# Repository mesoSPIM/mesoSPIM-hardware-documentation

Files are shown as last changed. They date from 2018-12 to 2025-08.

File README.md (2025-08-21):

## What is the mesoSPIM project?
The mesoSPIM (mesoscale selective plane illumination microscopy) project
aims at creating open-hardware microscopy platforms for imaging in cleared tissue. Core features of the mesoSPIM setups are:

* compatibilty with all tissue clearing techniques
* large field-of-views
* dual-sided excitation
* optimized for fast screening of whole mouse brain samples (10-14 GB/brain/color at low magnification, up to 100 GB/brain/color at high magnification)
* near-isotropic sampling (1.5-5 µm in X,Y and 3-6 µm in Z) due to an axially swept lightsheet which leads to uniform z-resolution across the field-of-view
* modular sample holders and quick sample exchange
* large travel range (50 x 50 x 100 mm) to allow imaging of very large samples

## Benchtop mesoSPIM
The [Benchtop mesoSPIM](https://github.com/mesoSPIM/benchtop-hardware) is the newest version and its repository is separate to organize documentation and wiki pages of the two very different systems.

## "Mainframe" mesoSPIM
The [mesoSPIM v.5 wiki](https://github.com/mesoSPIM/mesoSPIM-hardware-documentation/wiki) provides documentation, setup, and usage instructions of "mainframe" mesoSPIMs that require an optical table.

## mesoSPIM Version 6 "Revolver"
The detection arm of older versions (4 and 5) can be upgraded to a v.6 "Revolver" using the [following documentation](https://github.com/mesoSPIM/benchtop-hardware/tree/main/v4-5-upgrade-2023).

## mesoSPIM v.5
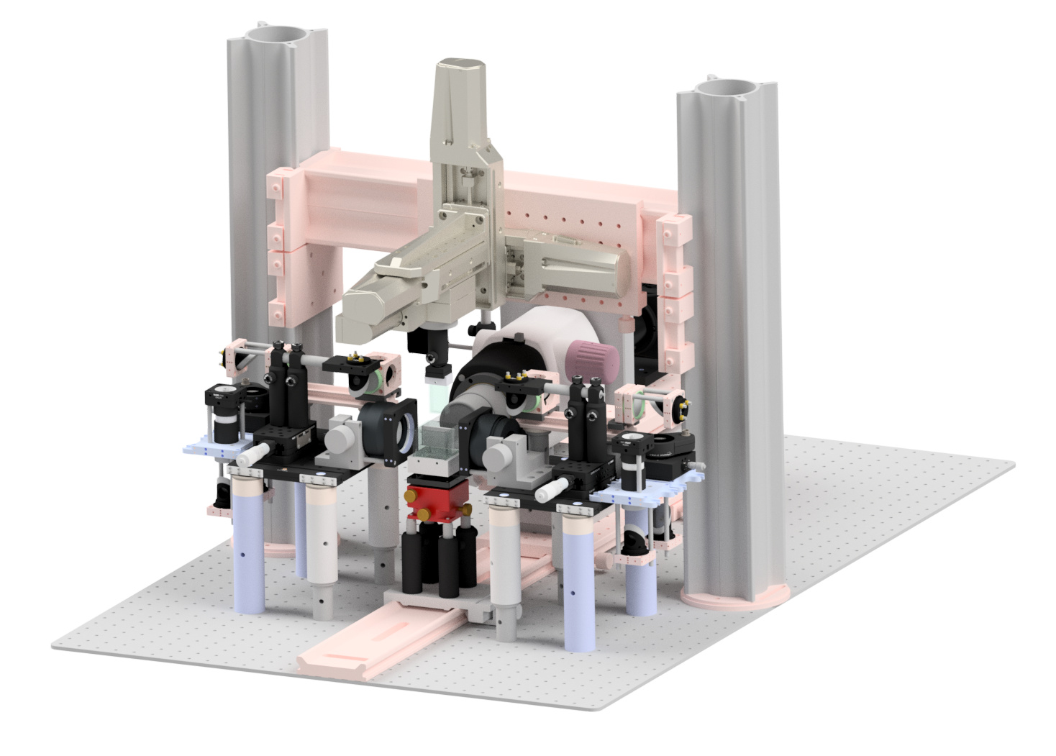
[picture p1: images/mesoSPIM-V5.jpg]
mesoSPIM V5


## Who is the mesoSPIM project for?
* You are looking for a versatile imaging platform for cleared tissue that can be tailored to your needs.
* Research groups and imaging facilities with experience in building and supporting custom microscopes.

## What are ideal imaging applications for a mesoSPIM?
* screening of large numbers of samples for clearing & labeling quality
* visualization of cell populations or other structures (blood vessels, plaques) in whole cleared organs

## What are the mesoSPIM instruments less well suited for?
* imaging live samples (this is the domain of classical light-sheet microscopes)
* high-resolution imaging (<1.5 µm optical resolution), e.g. subcellular structures.

## Not sure where to start?
You can start by comparing [Benchtop and V5](https://github.com/mesoSPIM/benchtop-hardware/tree/main) versions and deciding which one suites your needs better. When ready, review the respective Wiki pages and parts list. If still in doubt, contact us for help.

## About
See the project history and meet the developers on our [main website](https://mesospim.org/about/).

## Discussion
Since August 2025 we joined the vibrant [image.cs forum](https://forum.image.sc/tag/mesospim)



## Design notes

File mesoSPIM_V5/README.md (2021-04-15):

## Dimensional accuracy

Depending on manufacturing method, the dimensions of machined/3D printed part can deviate from the 
"perfect" fit to a glass cuvette or Thorlabs component.
Machined parts have dimensional accuracy typically 0.05 - 0.1 mm, 3D printed parts 0.1 - 0.2 mm 
and uneven surface finish.

Several iterations with dimension adjustment of model or part may be necessary to accomodate your 
particular manufacturing method.

For metal or plastic machining with [Protolabs](https://www.protolabs.com/), accuracy 0.1 mm should be expected.

For 3D printers (0.1-0.2 mm), see articles
* [3D Printer Dimensional Accuracy: 7 Tips & Tricks](https://all3dp.com/2/dimensional-accuracy-3d-printing-tips-tricks/).
* [Simplify3D: dimensional accuracy](https://www.simplify3d.com/support/print-quality-troubleshooting/dimensional-accuracy/)

Stereolitography printers (such as [Form3](https://formlabs.com/)) are more accurate than 
extrusion-filament ones.

## 3D printing materials
Sample holders for BABB/DBE/BB-PEG immersion should be printed from nylon (polyamide), because these are powerful organic solvents.

Parts that do not contact with solvents can be printed from common plastics (PLA, ABS). ABS is mechanically stronger than PLA.

## Post-processing
If you use 3D printing, threads usually have to be tapped manually, and small holes drilled, even if they are "printed".

## CAD software
Most of the models (ipt files) were generated in Autodesk Inventor (free educational version). 
Migration to free open-source software (FreeCAD, Blender, OpenSCAD) is planned for future releases.

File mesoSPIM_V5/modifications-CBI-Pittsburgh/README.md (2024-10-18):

# Improvements at the CBI Pittsburg
These modifications were made to V5 at the [CBI Pittsburg](https://cbi-pitt.webflow.io/). The following changes were made:

## 1. Improved Immersion Chamber
The mmersion chamber 3D printed using Formlabs Form 3 printer, with milled pockets for glass windows.

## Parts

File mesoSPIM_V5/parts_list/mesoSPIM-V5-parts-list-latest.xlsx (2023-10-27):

Part # | Vendor | Description | QTY | Unit Price (CHF) | Price (CHF) | Assembly | Subassembly | Comment
Optical Table
RS-2000 | Newport | RS-2000 Table | 1 | 8000 | 8000 | Optical Table |  | Needs to be selected according to needs & room configuration
Detection path: Major Components
C13440-20CU V3 | Hamamatsu | ORCA-FLASH 4.0 V3 CAMLINK | 1 | 16850.00 | 16850.00 | Detection path | Camera
N1564600 | Olympus | MVX-ZB10 Zoombody | 1 | 5950.00 | 5950.00 | Detection path | Olympus Microscope
N1564200 | Olympus | MVPLAPO1x Objective | 1 | 3180.00 | 3180.00 | Detection path | Olympus Microscope | The 2x works, but has large amounts of distortion
N1563500 | Olympus | MVX-TLU Tube lens | 1 | 1170.00 | 1170.00 | Detection path | Olympus Microscope
N1564500 | Olympus | MVX-TV1xC C-Mount Adapter | 1 | 303.00 | 303.00 | Detection path | Olympus Microscope
96A350 | Ludl | 96A350 10 pos Filter Wheel | 1 | 3016.94 | 3016.94 | Detection path | Filter wheel
996066 | Ludl | MAC6000 Controller | 1 | 3625.38 | 3625.38 | Detection path | Filter wheel
73006047 | Ludl | Keypad | 0 | 461.89 | 0.00 | Detection path | Filter wheel | Not strictly necessary
99A507 | Ludl | EMISSION FLANGE, OLYMPUS BX/IX Trinocular Mount | 1 | 335.55 | 335.55 | Detection path | Filter wheel
99A135 | Ludl | EMISSION FLANGE, OLYMPUS BX/IX Trinocular Mount | 1 | 335.55 | 335.55 | Detection path | Filter wheel
902-0064-000 | Nodna | Robotis Dynamixel MX-28R | 1 | 250.00 | 250.00 | Detection path | Zoom servo | Bought via nodna.de
903-0163-100 | Nodna | Robotis FR07-F101K Set Rotate Bracket (N101 Typ) | 1 | 45.00 | 45.00 | Detection path | Zoom servo | Bought via nodna.de
DX-C4-240 | Nodna | (DX-C4-240) Dynamixel DX/RX Cable 4-pin 240mm | 1 | 8.00 | 8.00 | Detection path | Zoom servo | Bought via nodna.de
P00001056 | Playzone | YF USB to RS485 Adapter | 1 | 12.50 | 12.50 | Detection path | Zoom servo | USB Adapter
Excitation path: Major Components
iChrome MLE-LFA-HP | Toptica | 405,488,561,640 nm, 100mW each, single fiber AFC | 2 | 51000.00 | 102000.00 | Excitation path | Laser | Alternatives include Omicron SOLE-6 with 2x AOM
BG-001943 | Toptica | MLE Passive Thermal Kit | 2 | 380.00 | 760.00 | Excitation path | Laser
BG-001977 | Toptica | MLE Active Thermal Kit | 0 | 1785.00 | 0.00 | Excitation path | Laser | Alternative to passive Kit for Toptica MLEs
GVS211/M | Thorlabs | 1D Large Beam (10 mm) Diameter Galvo System, Broadband Mirror (-E02), Metric, PSU Not Included | 2 | 1686.65 | 3373.30 | Excitation path | Scan unit | Only allows 10mm beam
GPS011 | Thorlabs | 1D or 2D Galvo System Linear Power Supply | 1 | 451.36 | 451.36 | Excitation path | Scan unit | Also used for the Scanlab scanners (order 2 in this case)
GCE001 | Thorlabs | Galvo Driver Card Cover | 2 | 56.15 | 112.30 | Excitation path | Scan unit | Only allows 10mm beam
136228 | Scanlab | Single-Axis-Module; 14/1; 450-2500nm, dynAXIS 3 M; SSV30; dynAXIS 3M without flange | 2 | 1842.00 | 3684.00 | Excitation path | Scan unit | Allows 14 mm beam, needs custom driver box, do not order for now, currently tested in Zurich
Sample & Microscope Stages
M-900K276 | Physik Instrumente | XYZRot System mesoSPIM V5.1 (2x L-509.20DG10, 1x L-509.40DG10, 1x M-060.DG) | 1 | 16100 | 16100 | Stages | Sample stage
C-884.6DC | Physik Instrumente | DC-Motor Controller, 6 CH | 1 | 5160 | 5160 | Stages | Controller
M-406.4PD | Physik Instrumente | Precision Translation Stage, 100mm | 1 | 4230 | 4230 | Stages | Detection focus
Computer
 | Brentford | Intel Xeon E5-2630V3, 128 GB RAM, Geforce 960, | 1 | 7827 | 7827 | Workstation
 | BenQ | BenQ BL3201PT 32" 4K LED UHD 3840x2160 | 1 | 1086 | 1086 | Screen
434494 | Digitec | Exsys EX-44094, Universal PCI-E zu 4S RS-232 Karte, (Oxford) | 1 | 86.9 | 86.9 | Microscope control |  | RS232/COM Card (Com ports are necessary for the filter wheel, possibly I stage, possibly other periphery)
6072231 | Digitec | Logitech G Saitek Farm Sim Vehicle Side Panel | 1 | 139 | 139 | Microscope control
Excitation path: Major optical components
EL-16-40-TC-VIS-5D-1-C | Optotune | EL16 Lenses | 2 | 1300 | 2600 | Excitation | ETL Unit
EL-E-4i | Optotune | Lens Driver | 2 | 270 | 540 | Excitation | ETL Unit | Have to be modified: BNC cables need to be soldered
CAB-6-300 | Optotune | Cables | 2 | 105 | 210 | Excitation | ETL Unit
 | Digitec | Powered USB-Hub | 1 | 30 | 30 | Excitation | ETL Unit | Simple USB-Hub for powering the ETL-Drivers
91863 | Nikon | Nikon AF-S 50 mm f/1.4 G | 2 | 469 | 938 | Excitation | Scan unit | Have to be modified
Detection: Emission Filters
F57-405SG | AHF | QuadLine Rejectionband ZET405/488/561/640 | 1 | 761.26 | 761.26 | Detection path |  | Filters have to be selected according to lasers & needs
F39-482SG | AHF | 482/35 BrightLine HC for CFP in SG32 (405 nm excitation) | 1 | 537.74 | 537.74 | Detection path |  | Filters have to be selected according to lasers & needs
F37-520SG | AHF | 520/35 BrightLine HC for EGFP in SG32 (488 nm Ex) | 1 | 537.74 | 537.74 | Detection path |  | Filters have to be selected according to lasers & needs
F37-542SG | AHF | 542/27 BrightLine HC for YFP in SG32 | 1 | 537.74 | 537.74 | Detection path |  | Filters have to be selected according to lasers & needs
F76-594SG | AHF | 594 LP Edge Basic Langpass-Filter in SG32 | 1 | 610.09 | 610.09 | Detection path |  | Filters have to be selected according to lasers & needs
F76-562SG | AHF | RazorEdge Sperrfilter LP 561 RU in SG32 | 1 | 1166.18 | 1166.18 | Detection path |  | Filters have to be selected according to lasers & needs
F39-508SG | AHF | 509/22 BrightLine HC in SG32 | 1 | 620.89 | 620.89 | Detection path |  | Filters have to be selected according to lasers & needs
F37-515SG | AHF | 515/LP BrightLine HC Langpass-Filter in SG32 | 1 | 733.18 | 733.18 | Detection path |  | Filters have to be selected according to lasers & needs
 | AHF | 535/30 ET Bandpass in SG32 | 1 | 467.77 | 467.77 | Detection path |  | Filters have to be selected according to lasers & needs
F47-450SG | AHF | 450/50 ET Bandpass in SG32 | 1 | 476.19 | 476.19 | Detection path |  | Filters have to be selected according to lasers & needs
F37-535SG | AHF | 530/43 Brightline HC in SG32 | 1 | 426.52 | 426.52 | Detection path |  | Filters have to be selected according to lasers & needs
F76-631SG | AHF | 633 LP Edge Basic in SG32 | 1 | 610.09 | 610.09 | Detection path |  | Filters have to be selected according to lasers & needs
F47-584SG | AHF | 585/40 ET Bandpass in SG32 | 1 | 476.19 | 476.19 | Detection path |  | Filters have to be selected according to lasers & needs
F37-565SG | AHF | 565/24 BrightLineHC in SG32 | 1 | 577.69 | 577.69 | Detection path |  | Filters have to be selected according to lasers & needs
Electronics / Signal generation
781161-01 | National Instruments | NI PXIe-1073 Integrated MXIe, 5 Periph Slots, PCIe-8361, 3m Cable | 1 | 1630 | 1630 | Signal generation
763065-01 | National Instruments | Power Cord, 220V, 10A, Swiss | 1 | 11 | 11 | Signal generation
779632-01 | National Instruments | PXI-6259 (32 Analog Inputs, 48 Digital I/O, 4 Analog Outputs) | 1 | 2800 | 2800 | Signal generation
777643-01 | National Instruments | BNC-2110 Noise Rejecting, Shielded BNC Connector Block | 3 | 520 | 1560 | Signal generation
192061-02 | National Instruments | SHC68-68-EPM Shielded Cable, 68-D-Type to 68 VHDCI Offset, 2 m | 2 | 193 | 386 | Signal generation
778512-01 | National Instruments | NI PXI-6733 with 8 16-Bit Waveform Analog Outputs | 1 | 3260 | 3260 | Signal generation
184749-02 | National Instruments | SH68-68-EP, Shielded Cable, 2 m | 1 | 186 | 186 | Signal generation
DELOCK 12498 | Reichelt | BNC to SMB cable, 3 m | 16 | 8.95 | 143.2 | Signal generation |  | SMB cables for Analog & Digital Laser control. A Sole-6 would require SMA cables
Excitation & detection path: Minor components
G022081000 | Qioptiq | Flat rail FLS 95-500-M | 2 | 119.86 | 239.72 | Detection Path | Detection Rail | 2nd Rail allows to park a stereomicroscope for visual inspection
G022083000 | Qioptiq | Flat rail FLS 95-1000-M | 1 | 222.44 | 222.44 | Detection Path | Main Rail | Main Rail the whole detection path, stages and sample rest on
G026106000 | Qioptiq | Profile X 95; 640 mm | 2 | 119.7 | 239.4 | Sample stages | Sample stage gantry
G026105000 | Qioptiq | Profile X 95; 500 mm | 1 | 101 | 101 | Sample stages | Sample stage gantry
G026206000 | Qioptiq | Baseplate X95 | 2 | 64 | 128 | Sample stages | Sample stage gantry
G026408000 | Qioptiq | Clamping carriage X-95 | 4 | 89.65 | 358.6 | Sample stages | Sample stage gantry
G063730000 | Qioptiq | Adjustable Mirror Insert 30 | 10 | 153.33 | 1533.32 | Excitation path | Fold mirrors | BBE1-E02 need to be glued to them
G061042000 | Qioptiq | Mounting Plate 30 | 10 | 27.00 | 269.95 | Excitation path | Fold mirrors
G061251000 | Qioptiq | Circlip Kit | 1 | 66.95 | 66.95 | Lab supplies | Excitation path | Special pliers in case the retaining rings of the Adjustable mirror insets 30 need to be removed
G061011000 | Qioptiq | Set of Threaded Pins M2.3x3, 150 ea. | 1 | 14.04 | 14.04 | Lab supplies | Excitation path
G061012000 | Qioptiq | Set of Threaded Pins M2.3x6 for Mounting Plates, 150 | 1 | 15.12 | 15.12 | Lab supplies | Excitation path
G061239000 | Qioptiq | Set of Special Screws M2.3x9 (20pcs.) | 1 | 30.23 | 30.23 | Lab supplies | Excitation path
G061238000 | Qioptiq | Set of Thumbscrews M2.3x4, 20 ea. | 1 | 24.84 | 24.84 | Lab supplies | Excitation path
G061111000 | Qioptiq | Set of Screws M2.3x5, (200pcs.) | 1 | 19.44 | 19.44 | Lab supplies | Excitation path
G061353000 | Qioptiq | Flat rail FLS 40-150 | 2 | 44.27 | 88.54 | Excitation path | Excitation path
G061374000 | Qioptiq | Carrier FLR 40-40 | 2 | 53.99 | 107.98 | Excitation path | Excitation relay | Mounting plate for Cube 30
G061047000 | Qioptiq | Mounting Plate 35 | 6 | 30.23 | 181.41 | Excitation path | Excitation relay | Mounts for 80 mm Achromats
G061081000 | Qioptiq | Cube 30 | 2 | 97.18 | 194.36 | Excitation path | Excitation relay | Mounts second to last fold mirror ahead of the scanners, have to be modified to allow a 35 mm lens to be mounted
G061225000 | Qioptiq | Holder 30 | 2 | 32.39 | 64.79 | Excitation path | Excitation relay | Mounts last fold mirror ahead of the scanners
G026529000 | Qioptiq | Carrier X 95-300, black, w/ hole pattern | 3 | 225.6782 | 677.0346 | Main Rail & Detection Path | Detection Rail | 1 for the focusing stage, 1 for the detection path, 1 for the XYZ stage assembly
G063200000 | Qioptiq | Achr. VIS ARB2; D=31.5; F=80; mounted | 4 | 158.73 | 634.92 | Excitation path | Excitation relay | Relay achromats from ETL to Scanners
G061372000 | Qioptiq | Carrier FLR 40-20 | 12 | 38.87 | 466.47 | Excitation path | Excitation relay | 2 in the excitation path, the rest are for alignment & spares
P100/M | Thorlabs | Ø1.5" Mounting Post M6 Taps L = 100 mm | 4 | 41.78 | 167.12 | Excitation path | Excitation platform
P150/M | Thorlabs | Ø1.5" Mounting Post M6 Taps L = 150 mm | 5 | 48.15 | 240.74 | Excitation path | Excitation platform
TBB1515/M | Thorlabs | Large-Area Translation Stage 150 mm x 191.7 mm | 2 | 483.60 | 967.20 | Excitation path | Excitation platform | Platforms the whole excitation path rests on
CPVM | Thorlabs | Vertical Cage System Mounting Plate | 4 | 41.27 | 165.08 | Excitation path | Excitation collimators & ETL
SHB025 | Thorlabs | Ø1/4" Stainless Steel Diaphragm Optical Beam Shutter with Controller | 2 | 833.86 | 1667.73 | Excitation path | Excitation collimators
SHCP025/M | Thorlabs | 30 mm Cage and Post Mounting Adapter for SHB025(T) Optical Beam Shutter M4 Tap | 2 | 37.30 | 74.60 | Excitation path | Excitation collimators | Mounting plate for shutters
SM1FCA | Thorlabs | FC/APC Fiber Adapter Plate with External SM1 (1.035"-40) Thread | 2 | 29.63 | 59.26 | Excitation path | Excitation collimators
CP02/M | Thorlabs | SM1-Threaded 30 mm Cage Plate 0.35" Thick 2 Retaining Rings M4 Tap | 2 | 15.77 | 31.53 | Excitation path | Excitation collimators | Cage plate to mount excitation collimator
ER05-P4 | Thorlabs | Cage Assembly Rod 1/2" Long Ø6 mm 4 Pack | 2 | 18.47 | 36.93 | Lab supplies | Excitation path
ER1-P4 | Thorlabs | Cage Assembly Rod 1" Long Ø6 mm 4 Pack | 2 | 18.47 | 36.93 | Lab supplies | Excitation path
ER1.5-P4 | Thorlabs | Cage Assembly Rod 1.5" Long Ø6 mm 4 Pack | 2 | 21.31 | 42.62 | Lab supplies | Excitation path
ER2-P4 | Thorlabs | Cage Assembly Rod 2" Long Ø6 mm 4 Pack | 4 | 22.32 | 89.27 | Lab supplies | Excitation path
ER3-P4 | Thorlabs | Cage Assembly Rod 3" Long Ø6 mm 4 Pack | 4 | 24.13 | 96.51 | Lab supplies | Excitation path
ER4-P4 | Thorlabs | Cage Assembly Rod 4" Long Ø6 mm 4 Pack | 4 | 25.94 | 103.75 | Lab supplies | Excitation path
SM1V10 | Thorlabs | Ø1" Adjustable Lens Tube 0.81" Travel Range | 2 | 32.01 | 64.02 | Excitation path | Excitation collimators
SM1L03-P5 | Thorlabs | SM1 Lens Tube 0.30" Thread Depth SM1RR Retaining Ring 5 Pack | 1 | 55.01 | 55.01 | Lab supplies | Excitation path
SM1L05-P5 | Thorlabs | SM1 Lens Tube 0.50" Thread Depth SM1RR Retaining Ring 5 Pack | 1 | 56.95 | 56.95 | Lab supplies | Excitation path
SM1L10-P5 | Thorlabs | SM1 Lens Tube 1.00" Thread Depth SM1RR Retaining Ring 5 Pack | 1 | 64.48 | 64.48 | Lab supplies | Excitation path
ST1XY-S | Thorlabs | XY Translator with Micrometer Drives | 2 | 355.56 | 711.11 | Excitation path | ETLs
XRN25C/M | Thorlabs | Compact 25 mm Travel Linear Translation Stage Rear Micrometer M6 Taps | 2 | 387.65 | 775.30 | Excitation path | Excitation path | Moves last fold mirror ahead of the scanners for light-sheet alignment
XRN-B1/M | Thorlabs | Baseplate for XRN25 Series Stages, Metric Slot Spacing | 2 | 30.18 | 60.36 | Excitation path | Excitation path
SM1A10 | Thorlabs | Adapter with External SM1 Threads and Internal C-Mount Threads | 2 | 18.41 | 36.83 | Lab supplies | Spare
SM1A9 | Thorlabs | Adapter with External C-Mount Threads and Internal SM1 Threads | 2 | 18.41 | 36.83 | Lab supplies | Spare
SM1A39 | Thorlabs | Adapter with External C-Mount Threads and External SM1 Threads | 2 | 19.68 | 39.37 | Excitation path | Excitation path | Connects ETLs to CPVM plate, very important
AC254-075-A-ML | Thorlabs | f=75 mm Ø1" Achromatic Doublet SM1-Threaded Mount ARC: 400-700 nm | 2 | 94.18 | 188.36 | Excitation path | Excitation collimators | Used as collimator to provide 15 mm beam-diameter
BBE1-E02 | Thorlabs | 1" Broadband Dielectric Elliptical Mirror 400 - 750 nm | 10 | 90.21 | 902.12 | Excitation path | Fold mirrors | Have to be glued to Qioptiq Adjustable Mirror Insert 30
SM2NFMA | Thorlabs | Adapter with External SM2 Threads and Nikon Female F-Mount Ring | 2 | 87.57 | 175.13 | Excitation path | Scan unit | Replaced discontinued SM2NFM part (update in 2023)
LCP31M | Thorlabs | 60 mm Blank Cage Plate M4 Tap | 2 | 34.39 | 68.78 | Excitation path | Scan unit | Mounting plate for the 50mm excitation objective. Replaced discontinued LCP03/M
RS2P/M | Thorlabs | Ø25.0 mm Pedestal Pillar Post M6 Taps L = 50 mm | 8 | 25.61 | 204.87 | Excitation path | Excitation relay and excitation platform
PS20/M | Thorlabs | Mounting Post Spacer, Height = 20 mm | 8 | 11.54 | 92.32 | Excitation path | Excitation platform
PS5M | Thorlabs | Mounting Post Spacer Height = 5 mm | 4 | 8.10 | 32.38 | Excitation path | Excitation relay
PS3/M | Thorlabs | Mounting Post Spacer, Height = 3 mm | 8 | 11.54 | 92.32 | Excitation path | Excitation platform
RS3P/M | Thorlabs | Ø25.0 mm Pedestal Pillar Post M6 Taps L = 75 mm | 2 | 28.04 | 56.08 | Excitation path | Excitation relay
RS3M | Thorlabs | Ø25 mm Post Spacer Thickness = 3 mm | 6 | 7.04 | 42.22 | Detection path | Camera Mount
RS10M | Thorlabs | Ø25 mm Post Spacer Thickness = 10 mm | 2 | 8.15 | 16.30 | Lab supplies | Spare
PH50/M | Thorlabs | Ø12.7 mm Post Holder Spring-Loaded Hex-Locking Thumbscrew L=50 mm | 4 | 7.48 | 29.93 | Lab supplies | Excitation path
PH75/M | Thorlabs | Ø12.7 mm Post Holder Spring-Loaded Hex-Locking Thumbscrew L=75 mm | 3 | 7.87303776 | 23.61911328 | Lab supplies | Excitation path
PH150/M | Thorlabs | Ø12.7 mm Post Holder Spring-Loaded Hex-Locking Thumbscrew L=150 mm | 1 | 12.04 | 12.04 | Lab supplies | Excitation path
TPSM1/M | Thorlabs | Magnetic Laser Safety Screen, 200 mm x 75 mm, Metric Engraving | 6 | 32.00 | 192.00 | Laser safety | Laser safety | General-purpose magnetic beam blocks, very useful
TPSM2/M | Thorlabs | Magnetic Laser Safety Screen, 300 mm x 75 mm, Metric Engraving | 6 | 40.25 | 241.50 | Laser safety | Laser safety | General-purpose magnetic beam blocks, very useful
RA180/M-P5 | Thorlabs | Right-Angle End Clamp for Ø1/2" Posts, M6 Stud and 5 mm Hex, 5 Pack | 2 | 57.50 | 115.00 | Lab supplies | Excitation path + Spare
RA90/M-P5 | Thorlabs | Right-Angle Clamp for Ø1/2" Posts, 5 mm Hex, 5 Pack | 2 | 51.01 | 102.02 | Lab supplies | Excitation path + Spare
TR50/M-P5 | Thorlabs | Ø12.7 mm Optical Post, SS, M4 Setscrew, M6 Tap, L = 50 mm, 5 Pack | 5 | 24.41 | 122.05 | Lab supplies | Excitation path + Spare
TR75/M-P5 | Thorlabs | Ø12.7 mm Optical Post, SS, M4 Setscrew, M6 Tap, L = 75 mm, 5 Pack | 2 | 26.16 | 52.32 | Lab supplies | Excitation path + Spare
TR100/M-P5 | Thorlabs | Ø12.7 mm Optical Post, SS, M4 Setscrew, M6 Tap, L = 100 mm, 5 Pack | 2 | 27.62 | 55.24 | Lab supplies | Excitation path + Spare
TR150/M-P5 | Thorlabs | Ø12.7 mm Optical Post, SS, M4 Setscrew, M6 Tap, L = 150 mm, 5 Pack | 2 | 33.06 | 66.12 | Lab supplies | Excitation path + Spare
TR250/M | Thorlabs | Ø12.7 mm Optical Post SS M4 Setscrew M6 Tap L = 250 mm | 1 | 8.59 | 8.59 | Detection Path | Servo mount
PH50/M-P5 | Thorlabs | Ø12.7 mm Post Holder, Spring-Loaded Hex-Locking Thumbscrew, L=50 mm, 5 Pack | 1 | 40.25 | 40.25 | Lab supplies | Excitation path + Spare
PH75/M-P5 | Thorlabs | Ø12.7 mm Post Holder, Spring-Loaded Hex-Locking Thumbscrew, L=75 mm, 5 Pack | 1 | 43.23 | 43.23 | Lab supplies | Excitation path + Spare
PH100/M-P5 | Thorlabs | Ø12.7 mm Post Holder, Spring-Loaded Hex-Locking Thumbscrew, L=100 mm, 5 Pack | 1 | 47.93 | 47.93 | Lab supplies | Excitation path + Spare
BA2/M-P5 | Thorlabs | Mounting Base, 50 mm x 75 mm x 10 mm, 5 Pack | 1 | 34.34 | 34.34 | Lab supplies | Excitation path + Spare
BA1S/M-P5 | Thorlabs | Mounting Base, 25 mm x 58 mm x 10 mm, 5 Pack | 1 | 24.46 | 24.46 | Lab supplies | Excitation path + Spare
PSHA/M | Thorlabs | Adjustable Height Collar M6 Locking Screw | 1 | 61.64 | 61.64 | Detection path | Camera Mount
C1515/M | Thorlabs | Ø1.5" Mounting Post Bracket M6 Taps | 1 | 95.24 | 95.24 | Detection path | Camera Mount
XT95P3 | Thorlabs | Base Plate for 95 mm Rails | 1 | 48.68 | 48.68 | Detection path | Camera Mount | Needs to be modified
KB25/M | Thorlabs | Complete 25 mm x 25 mm Kinematic Base Top and Bottom Plates M4 Counterbores | 10 | 74.34 | 743.39 | Sample mounts | Sample holder | It's always good to have more of these - depending on the number of samples & cuvettes - also for intermediate storage of samples
CP20S | Thorlabs | 30 mm Cage System Iris Ø20.0 mm Maximum Aperture | 2 | 83.60 | 167.20 | Excitation path | Excitation collimators
CF125C/M-P5 | Thorlabs | Clamping Fork 31.5 mm Counterbored Slot M6 x 1.0 Captive Screw 5 Pack | 1 | 49.13 | 49.13 | Lab supplies | Excitation path
PH20/M | Thorlabs | 12.7 mm Post Holder, Spring-Loaded Hex-Locking Thumbscrew, L=20 mm | 2 | 6.84 | 13.67 | Sample holder | Sample holder
TR20/M-P5 | Thorlabs | Stainless Steel Optical Posts - Metric | 1 | 20.73 | 20.73 | Sample holder | Sample holder
CL5A-P5 | Thorlabs | Table Clamp, L-Shape, Rounded Lip, 5 Pack | 1 | 19.8 | 19.8 | Sample Stage | Sample stage gantry
L200/M | Thorlabs | 4" x 3" Lab Jack, 1.03" Vertical Travel, 50 lbs Load Capacity, Metric | 1 | 462 | 462 | Sample mounts | Sample mounts | Order one for each planned immersion cuvette mount (e.g. 40x40 or 50x50)
LX10/M | Thorlabs | Self-Contained 25 mm Translation Stage, M6 Taps | 1 | 530.00 | 530.00 | Sample mounts | Sample mounts | Order one for each planned immersion cuvette mount (e.g. 40x40 or 50x50) if optical path adjustment is desired
UBP2/M | Thorlabs | Universal Base Plate, 65 mm x 65 mm x 10 mm, Metric | 1 | 38.54 | 38.54 | Sample mounts | Sample mounts | Order one for each planned immersion cuvette mount (e.g. 40x40 or 50x50) if optical path adjustment is desired
M-360-90 | Newport | Angle Bracket, 90°, Slotted Faces, Metric | 1 | 82.00 | 82.00 | Detection path | Camera bracket
M-CXL95-120 | Newport | Rail Carriage, 120 mm Length, M5 and M6 Thread, X95 Series | 4 | 127.00 | 508.00 | Sample mounts | Sample holder and general supplies | Sample holder and general supplies - it is useful to have more of these for exchanging the outer cuvettes
M-CXL95-50 | Newport | Rail Carriage, 50 mm Length, M6 Thread, X95 Series | 2 | 95.00 | 190.00 | Detection path | Servo holder & spare | Servo holder & spare
RD-PDT-B | Radiant Dyes | Tip-Tilt Plate | 2 | 280.00 | 560.00 | Sample holder | Sample holder | Order one for each planned immersion cuvette mount (e.g. 40x40 or 50x50)
Alignment Tools
SI254 | Thorlabs | Shearing Interferometer with a 10-25.4 mm Beam Diameter Shear Plate | 1 | 488.00 | 488.00
SI100P | Thorlabs | Shear Plate, 5-10 mm Beam Diameter | 1 | 184.00 | 184.00
SICP | Thorlabs | 30 mm Cage System Adapter for Shearing Interferometers with Diffuser Viewing Screen | 1 | 76.00 | 76.00
CCM1-G01/M | Thorlabs | 30 mm Cage Cube-Mounted Protected Aluminum Turning Mirror, M4 Tap | 1 | 184.00 | 184.00
SM1FC | Thorlabs | FC/PC Fiber Adapter Plate with External SM1 (1.035"-40) Thread | 1 | 31.00 | 31.00
SM1FCA | Thorlabs | FC/APC Fiber Adapter Plate with External SM1 (1.035"-40) Thread | 1 | 32.78 | 32.78
AC254-100-A-ML | Thorlabs | f=100 mm Ø1" Achromatic Doublet SM1-Threaded Mount ARC: 400-700 nm | 1 | 94.18 | 94.18
SM1V15 | Thorlabs | Ø1" Adjustable Lens Tube, 1.31" Travel Range | 1 | 36.80 | 36.80
SM1M20 | Thorlabs | SM1 Lens Tube Without External Threads, 2" Long, Two Retaining Rings Included | 1 | 17.00 | 17.00
SM1T2 | Thorlabs | SM1 (1.035"-40) Coupler, External Threads, 0.5" Long | 2 | 21.21 | 42.42
DGM05 | Thorlabs | Digital Indicator | 1 | 304.75 | 304.75 |  |  | Very useful
DIGC6 | Thorlabs | Digital Calipers | 1 | 148.21 | 148.21 |  |  | Very useful
R2L2S3P2 | Thorlabs | Grid Distortion Target, 1.5" x 1.5", 250 µm Grid Spacing | 1 | 348.45 | 348.45 |  |  | Very useful
FFM1 | Thorlabs | 30-mm-Cage-Compatible Rectangular Filter Mount | 1 | 60.95 | 60.95
DG10-1500-H1-MD | Thorlabs | Ø1" SM1-Mounted Frosted Glass Alignment Disk w/Ø1 mm Hole | 1 | 34.50 | 34.50 |  |  | Nice to have
DG20-1500-H2-MD | Thorlabs | Ø2" SM2-Mounted Frosted Glass Alignment Disk w/Ø2 mm Hole | 1 | 51.45 | 51.45 |  |  | Nice to have
CPA1 | Thorlabs | 30 mm Cage System Alignment Plate with Ø1 mm Hole | 2 | 13.80 | 27.60
LCPA1 | Thorlabs | 60 mm Cage Alignment Plate | 1 | 19.09 | 19.09
LCP01/M | Thorlabs | 60 mm Cage Plate, SM2 Threads, 0.5" Thick, M4 Tap (Two SM2RR Retaining Rings Included) | 2 | 40.51 | 81.02 |  |  | Nice to have as spares
CP20S | Thorlabs | 30 mm Cage System Iris Ø20.0 mm Maximum Aperture | 2 | 83.60 | 167.20 |  |  | Nice to have
SM1D12D | Thorlabs | SM1 Ring-Actuated Iris Diaphragm (Ø0.8 - Ø12 mm) | 4 | 70.10 | 280.42 |  |  | Nice to have
G061008000 | Qioptiq | Mounting Plate Without Hole | 2 | 28.75 | 57.50 |  |  | Have to be modified with SM1 threads
G061372000 | Qioptiq | Carrier FLR 40-20 | 2 | 38.87 | 77.75
 | Fisso | Strato M-28 movable arm | 1 | 205.00 | 205.00 |  |  | Very useful
 | Fisso | Thread adapter female M8/ male M6 thread reduction for Fisso | 2 | 12.00 | 24.00 |  |  | Very useful
General lab supplies
LAB-16 | Newport | Ultra Jet Canned Air Duster, 10 oz. (300ml) | 4 | 16.50 | 66.00 |  |  | Or other canned duster
Optical Wonder | Baader Planetarium | Microfiber cloth, Optical Wonder | 4 | 7.47 | 29.88 |  |  | General cleaning cloth for non-risky surfaces (Eyepieces etc)
19569/16OZ | Cargille | Immersion oil from cargille for Clarity: Code 50350 nD=1.4587 fused silica matching oil | 2 | 140.00 | 280.00 |  |  | A decent supply is recommend (though it is not consumed much)
13023MPRM2.5 | Kummer | EPO-TEK 302-3M in 2.5 g pre-pack, burst seal, 25x packs (minimum order) | 1 | 438.00 | 438.00 |  |  | 1 2.5g package is sufficent to glue 10 mirrors, Fabian will take care of that
MC-50E | Thorlabs | Lens Tissues, 25 Sheets per Booklet, 50 Booklets in a Closeable Box | 1 | 85.10 | 85.10
ESK11 | Thorlabs | BNC Adapters Essentials Kit, 62 Pieces | 1 | 914.00 | 914.00 |  |  | This or any other BNC-Kit with all the common connectors (e.g. T, L, Straight etc.)
CA2848 | Thorlabs | SMA Coaxial Cable, SMA Male to BNC Male, 48" (1219 mm) | 2 | 18.00 | 36.00 |  |  | Sometimes useful
2249-C-120 | Thorlabs | 0.3 m BNC Cable | 4 | 15.25 | 61.00
2249-C-24 | Thorlabs | 0.6 m BNC Cable | 10 | 16.50 | 165.00
2249-C-60 | Thorlabs | 1.5 m BNC cable | 10 | 24.00 | 240.00
2249-C-120 | Thorlabs | 3m BNC cable | 6 | 24.00 | 144.00
BKF12 | Thorlabs | Black Aluminium Foil | 2 | 32.00 | 64.00 |  |  | Sometimes useful
PLT2 | Thorlabs | Ø1/2" (Ø12.7 mm) Photoluminescent Stickers, Qty: 100 | 1 | 25.00 | 25.00 |  |  | Sometimes useful for marking setups in darkness
T743-2.0 | Thorlabs | High-Performance Black Masking Tape, 2" x 180' (50 mm x 55 m) Roll | 2 | 51.58 | 103.16
PSS7 | Thorlabs | 7-Piece Precision Screwdriver Set | 1 | 60.00 | 60.00 |  |  | Or other, cheaper sets
HW-KIT6/M | Thorlabs | Imperial Screw Thread Adapter Kit | 1 | 136.48 | 136.48
HW-KIT6/M | Thorlabs | Metric Screw Thread Adapter Kit | 1 | 136.48 | 136.48
HW-KIT1/M | Thorlabs | M4 Cap Screw and Hardware Kit | 1 | 60.95 | 60.95
HW-KIT3/M | Thorlabs | M4 Setscrew and Hardware Kit | 1 | 119.42 | 119.42
HW-KIT4/M | Thorlabs | M6 Setscrew and Hardware Kit | 1 | 105.80 | 105.80
HW-KIT2/M | Thorlabs | M6 Cap Screw and Hardware Kit | 2 | 119.60 | 239.20
TC3/M | Thorlabs | 15-Piece Balldriver and Hex Key Kit with Stand, Metric | 2 | 92.00 | 184.00
TC2 | Thorlabs | 20-Piece Balldriver and Hex Key Kit with Stand, Imperial | 1 | 96.23 | 96.23
SPW801 | Thorlabs | Adjustable Spanner Wrench | 1 | 102.44 | 102.44
SPW602 | Thorlabs | SM1 Spanner Wrench, Graduated, Length = 3.88" | 2 | 28.00 | 56.00
 |  | Multiport-power outlets | 4
 |  | Swiss power cords to standard cold-device plugs | 10
 |  | Cable wraps | 1 |  |  |  |  | Lots of them
 |  | Isopropanol p.a. for lens cleaning | 1
Custom components
 | Mechanical Workshop | Galvomount-22mm-diameter-Thorlabs-Left.ipt | 1 |  |  | Excitation Path |  | Only if Thorlabs Scanners are used | Aluminium
 | Mechanical Workshop | Galvomount-22mm-diameter-Thorlabs-Right.ipt | 1 |  |  | Excitation Path |  | Only if Thorlabs Scanners are used | Aluminium
 | Mechanical Workshop | Galvomount-22mm-diameter-Left-Scanlab-V4.ipt | 0 |  |  | Excitation Path |  | Only if Scanlab Scanners are used, parts under test at HIFO, will require additional parts | Aluminium
 | Mechanical Workshop | Galvomount-22mm-diameter-Right-Scanlab-V4.ipt | 0 |  |  | Excitation Path |  | Only if Scanlab Scanners are used, parts under test at HIFO, will require additional parts | Aluminium
 | Mechanical Workshop | LCP31M-Nikon-modified4ThorlabsSM2NFMA(v2023).ipt | 2 |  |  | Excitation Path |  | Modified LCP31M | Aluminium
 | Mechanical Workshop | MVX-10-Bracket-V5.ipt | 1 |  |  | Detection Path |  |  | Aluminium
 | Mechanical Workshop | Servo-Dynamixel-Adapter-V2.ipt | 1 |  |  | Detection Path |  |  | Brass
 | Mechanical Workshop | Large-cuvette-mount-30mm-V1.ipt | 0 |  |  | Sample Mounts |  | if 30 mm cuvettes are desired | POM (Polyoxymethylen)
 | Mechanical Workshop | Large-cuvette-mount-40mm-V3.ipt | 2 |  |  | Sample Mounts |  | Order one for each planned immersion cuvette mount / imaging medium | POM (Polyoxymethylen)
 | Mechanical Workshop | Large-cuvette-mount-50mm-V3.ipt | 2 |  |  | Sample Mounts |  | Order one for each planned immersion cuvette mount / imaging medium | POM (Polyoxymethylen)
 | Mechanical Workshop | M-060-Adapter.ipt | 1 |  |  | Sample Mounts |  |  | Aluminium
Will be redesigned | Mechanical Workshop | Sample-cuvette-clamp-20mm-V3.ipt | 10 |  |  | Sample Mounts |  | Redesign is being worked on | POM (Polyoxymethylen)
 | Mechanical Workshop | Cube_30_with_35mm_hole | 2 |  |  | Excitation Path |  |  | Aluminium
 | Mechanical Workshop | M605-to-X95-adapter-V1 | 1 |  |  | Detection Path |  |  | Aluminium
 | Mechanical Workshop | X95carrier-to-M605-adapter-V1 | 1 |  |  | Detection Path |  |  | Aluminium
 | Mechanical Workshop | XT95P3_X95_Base_plate_mod | 1 |  |  | Detection Path |  | Modified XT95P3 | Aluminium
Sample cuvettes
 | Portmann Instruments | UQ-205-H80 10x20x80 | 0 | 518.5 | 0 |  |  | Whole-Mouse CNS Cuvettes
 | Portmann Instruments | UQ-753-H100 40x40x100 | 0 | 764 | 0
 | Portmann Instruments | UQ-205-H120 10x20x120 | 0 | 816 | 0 |  |  | Whole-Mouse CNS Cuvettes
 | Portmann Instruments | UQ-753-H120 40x40x120 | 0 | 952 | 0
 | Portmann Instruments | UQ-751 20x20 mm | 0 | 99.5 | 0
 | Portmann Instruments | UQ-752 30x30 | 0 | 128.5 | 0
 | Portmann Instruments | UQ-753 40x40 | 0 | 156 | 0
 | Portmann Instruments | UQ-754 50x50 | 0 | 184.5 | 0
 | Portmann Instruments | UQ-203 5x10x45 | 0 | 106.5 | 0
 | Portmann Instruments | UQ-204 10x10x45 | 6 | 106.5 | 639
 | Portmann Instruments | UQ-205 10x20x45 | 10 | 121.5 | 1215 |  |  | Standard cuvette for mouse brains & CLARITY
Fun Stuff
 | sygns.de | Custom Neon | mesospim.org | Classic Red | 100cm on white matte Aluminium | 1 | 932 | 932 | Neon Sign |  | This is the glowing red "mesospim.org" neon sign, can be identical to order DE176398
 |  |  |  | SUM | 238763.06

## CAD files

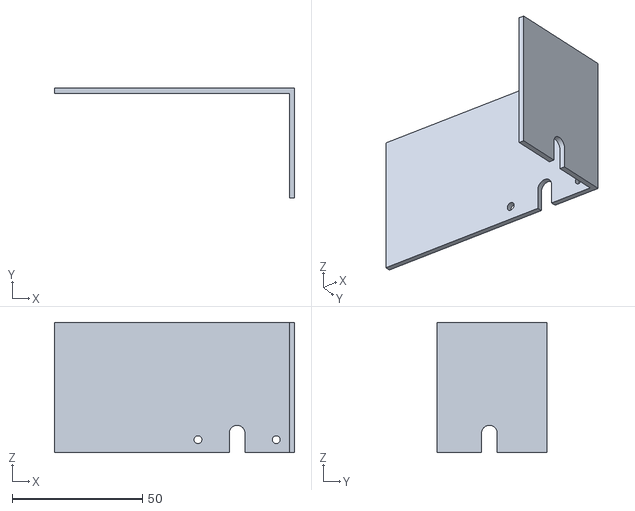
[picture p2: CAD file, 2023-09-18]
mesoSPIM_V5/freeCAD_files/laser_covers/excitation-miror-cover-LEFT-Body.stl
92.0 x 42.0 x 50.0

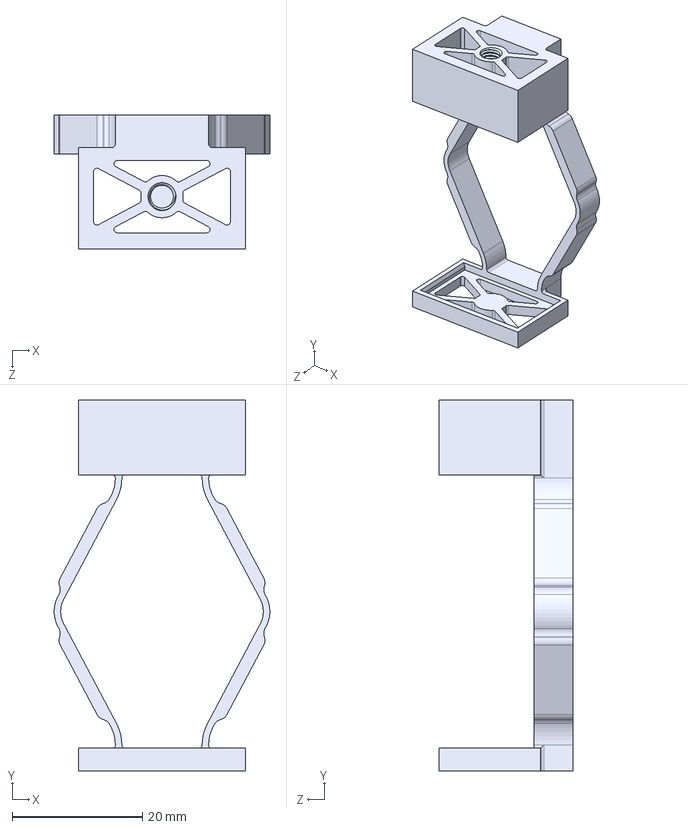
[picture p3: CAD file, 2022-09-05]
mesoSPIM_V5/inventor_files/cuvette-clamp-compliant/Clamp-UG205(204)_100881(1mm Gelenke 2Stk.)_B.step
33.1 x 57.0 x 20.6 mm

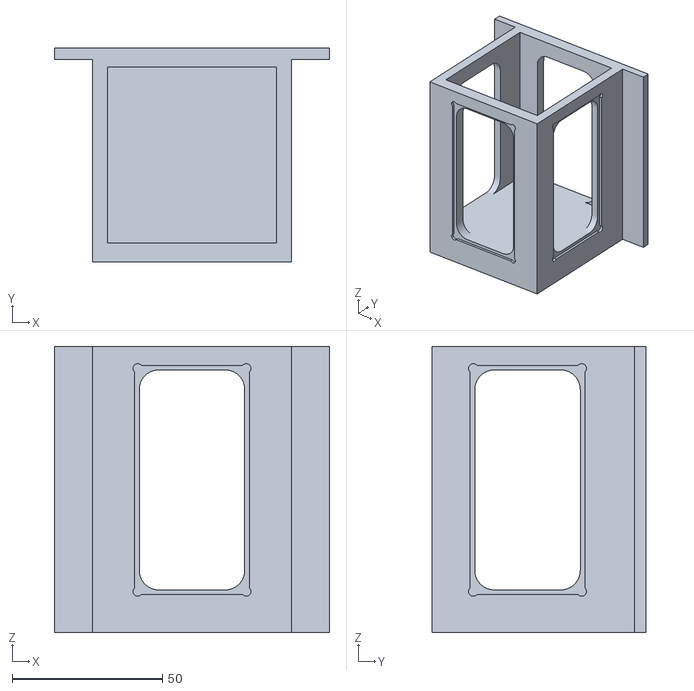
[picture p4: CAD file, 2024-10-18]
mesoSPIM_V5/modifications-CBI-Pittsburgh/ImmersionChamber/chamber-DLP-printed.STL
91.4 x 71.1 x 95.2

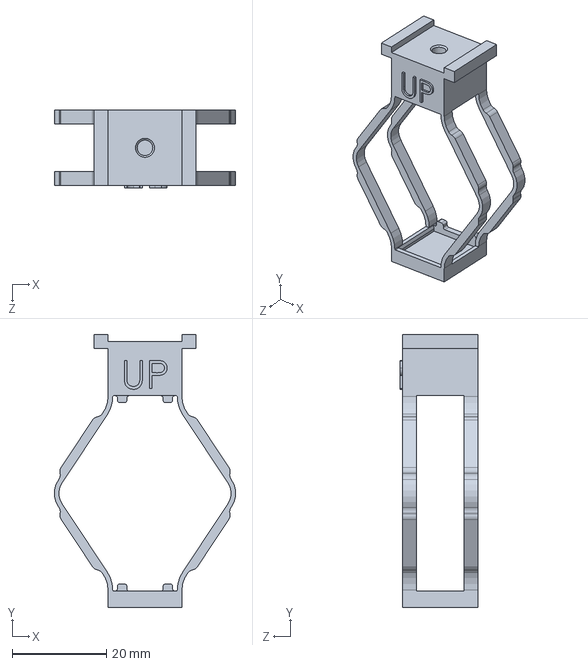
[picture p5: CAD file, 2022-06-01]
mesoSPIM_V5/solid_works_files/cuvette-clamp-compliant/compliant-AddManDesign-D100129.SLDPRT
38.5 x 58.0 x 16.6 mm

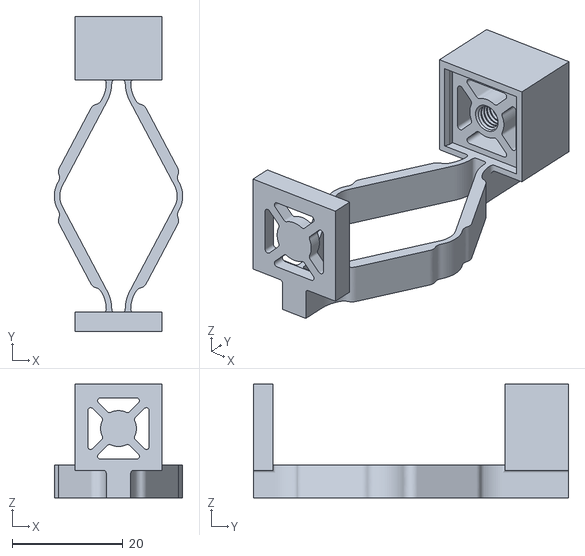
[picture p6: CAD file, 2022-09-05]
mesoSPIM_V5/stl_files/cuvette-clamp-compliant/Clamp-UG205(204)_100881(Quadratisch Gelenke 2 Stk.)_B.stl
23.2 x 57.0 x 20.6

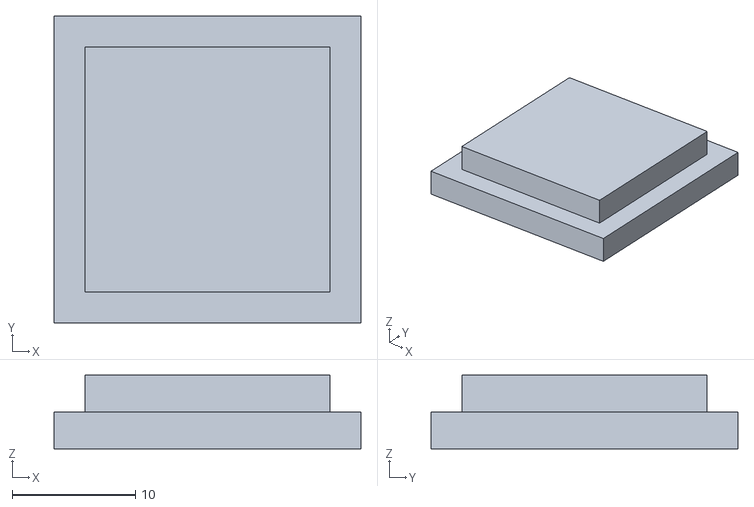
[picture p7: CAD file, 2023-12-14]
mesoSPIM_V5/stl_files/Large-cuvette-cap-25mm.stl
24.9 x 24.9 x 6.00

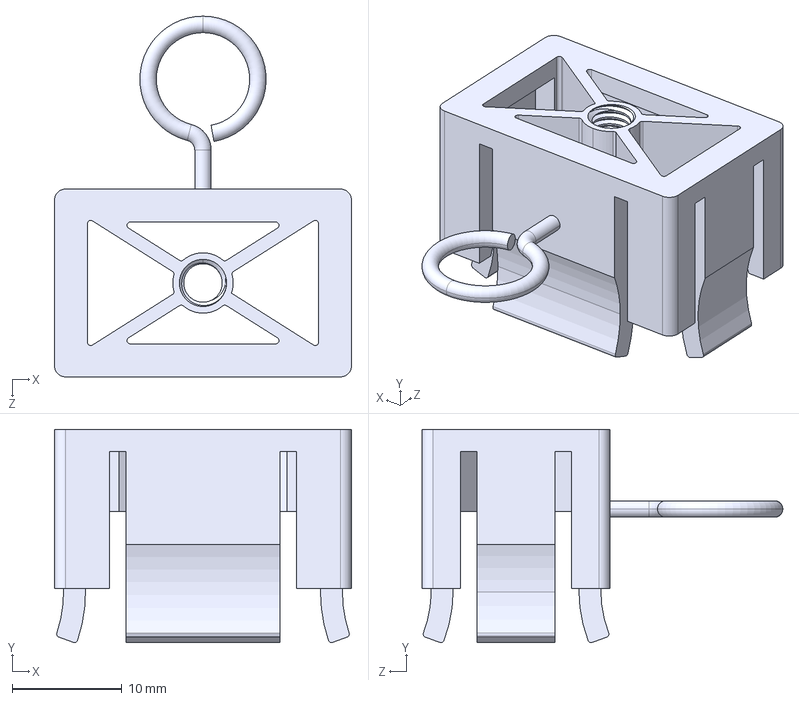
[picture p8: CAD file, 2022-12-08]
mesoSPIM_V5/stp_files/cuvette-clamp-compliant/TopClamp-UG205_100943(Rechteck 2mm)_D.step
27.1 x 19.4 x 32.9 mm

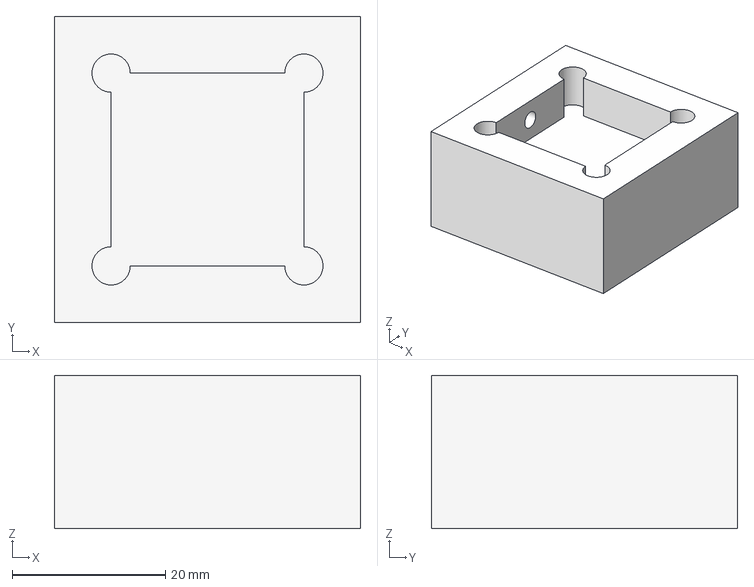
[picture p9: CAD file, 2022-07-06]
mesoSPIM_V5/stp_files/Large-cuvette-mount-25mm-V3.stp
40.0 x 40.0 x 20.0 mm

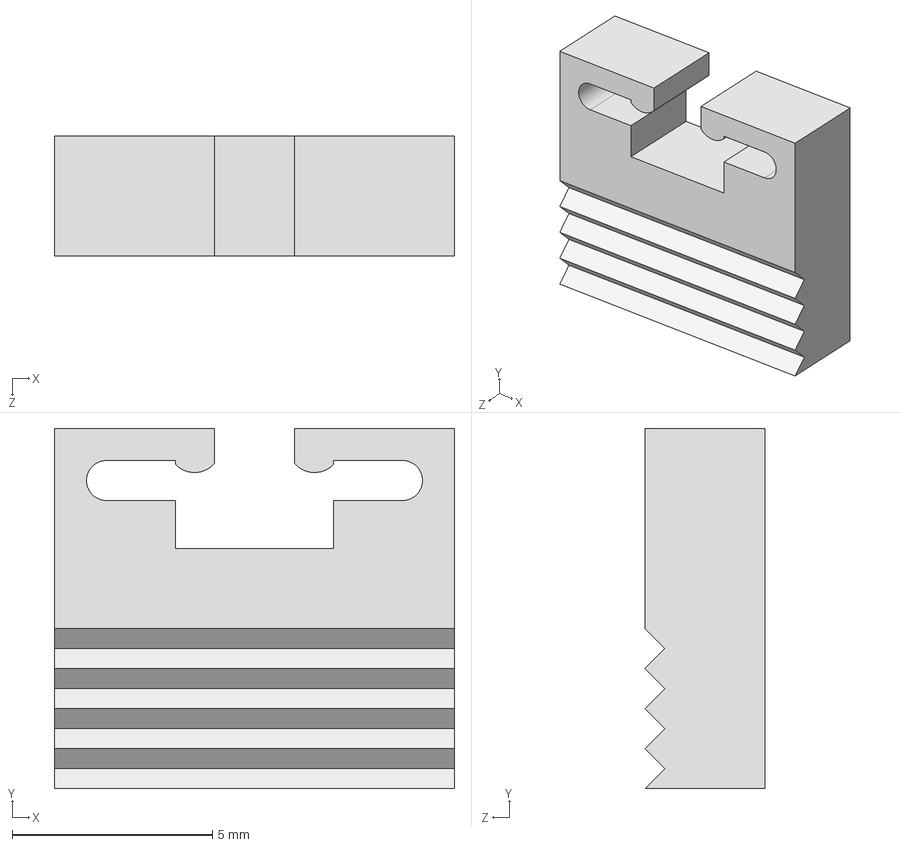
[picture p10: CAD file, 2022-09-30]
mesoSPIM_V5/stp_files/sample-clamp/Clamp-part2(moving)-Base9x10mm_flexible.step
10.0 x 9.00 x 3.00 mm

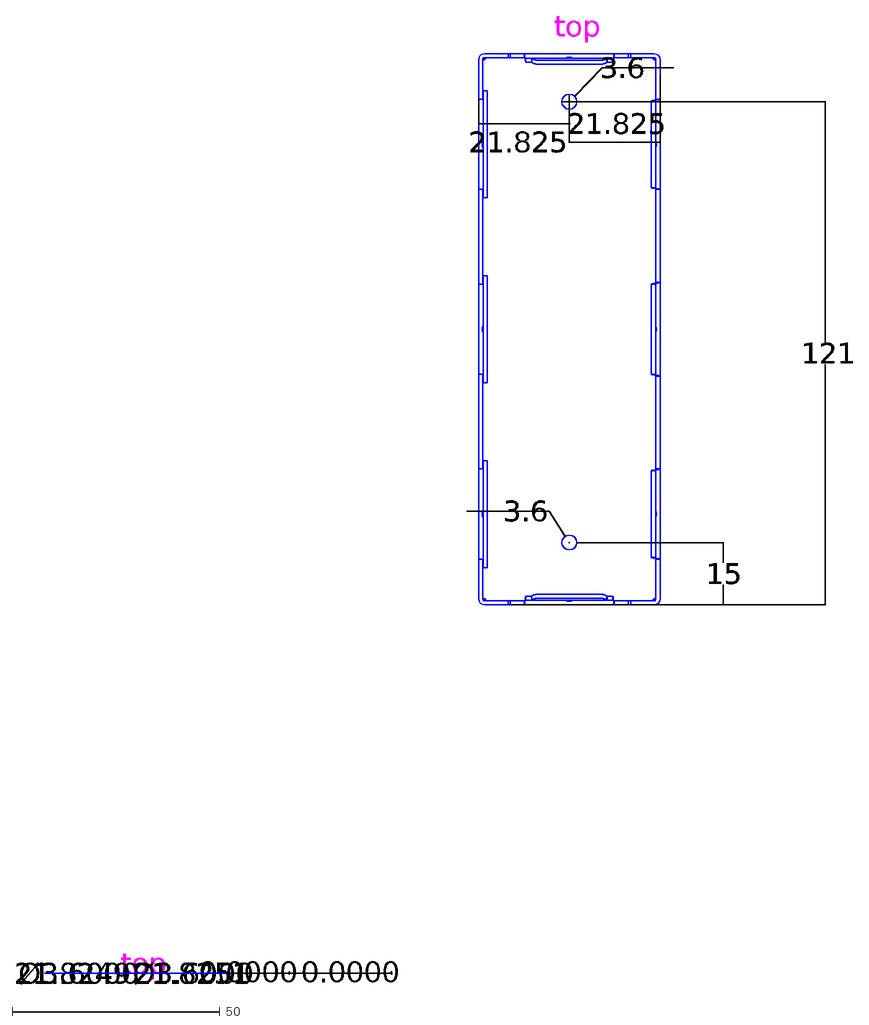
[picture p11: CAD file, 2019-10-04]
scanlab_galvo_upgrade/drawings/Gehäuse 15.1 back.dxf
top
15
121
21.825
3.6
0.0000
21.8249
21.8251
Ø3.6000

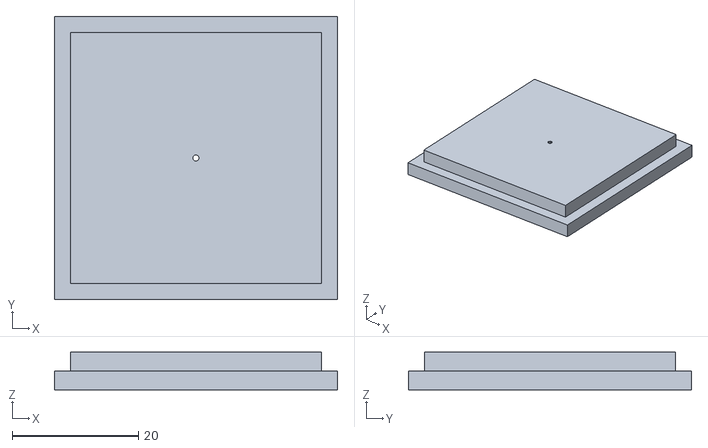
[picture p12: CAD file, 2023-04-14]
mesoSPIM_V5/stl_files/Large-cuvette-cap-40mm.stl
44.9 x 44.9 x 6.00

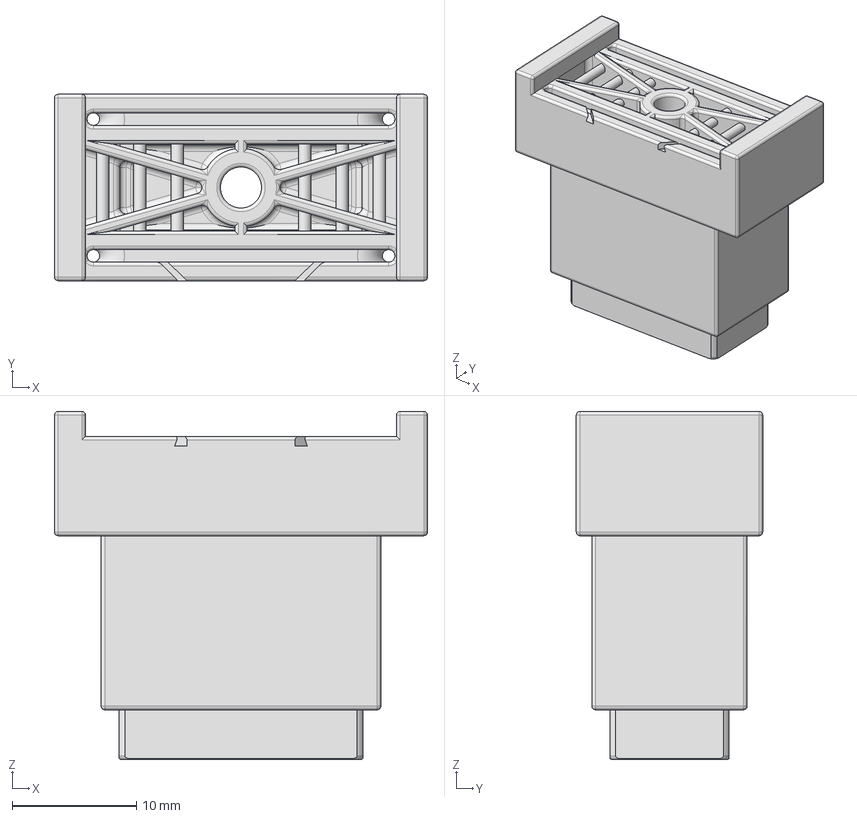
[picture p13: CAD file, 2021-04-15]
mesoSPIM_V5/stp_files/10x20mm_Cuvette_Top_V5_Sascha.stp
30.0 x 15.0 x 28.0 mm

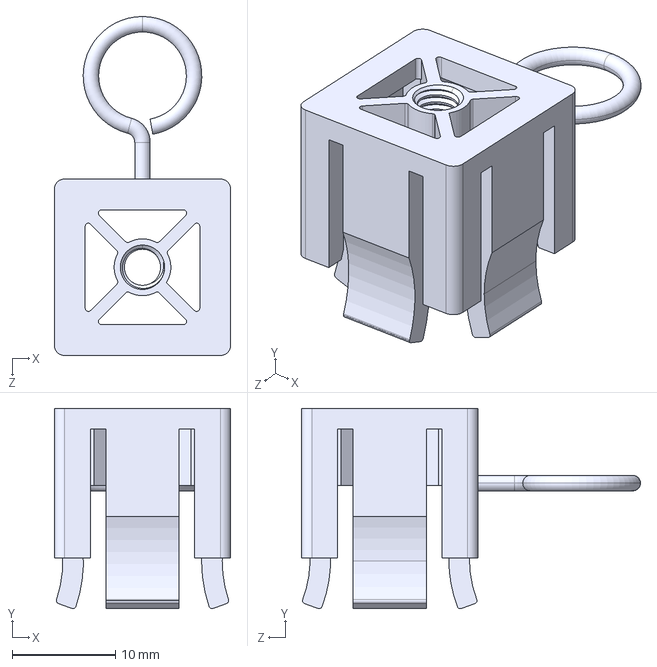
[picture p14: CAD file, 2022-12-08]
mesoSPIM_V5/stp_files/cuvette-clamp-compliant/TopClamp-UG204_100943(Quadrat 2mm)_D.step
17.1 x 19.4 x 32.9 mm

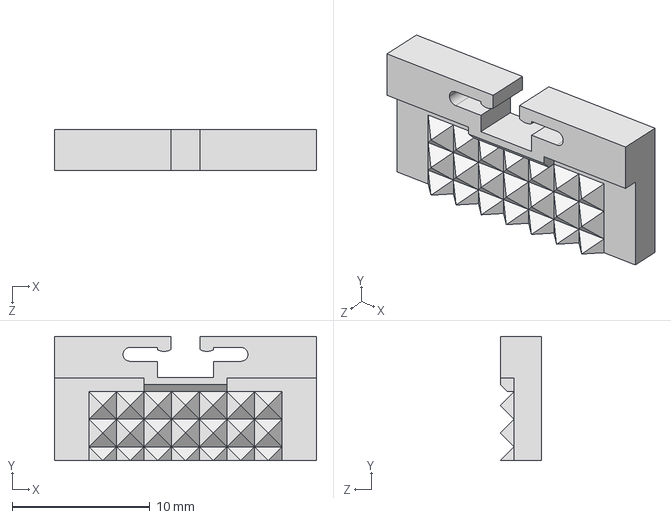
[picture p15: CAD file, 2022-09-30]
mesoSPIM_V5/stp_files/sample-clamp/Clamp-part2(moving)-Base9x19mm_flexible.step
19.0 x 9.00 x 3.00 mm

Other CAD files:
mesoSPIM_V5/freeCAD_files/laser_covers/excitation-miror-cover-LEFT.FCStd
mesoSPIM_V5/inventor_files/cuvette-clamp-compliant/Clamp-UG205(204)_100881(Quadratisch Gelenke 2 Stk.)_B.step
mesoSPIM_V5/stl_files/cuvette-clamp-compliant/Clamp-UG205(204)_100881(1mm Gelenke 2Stk.)_B.stl
scanlab_galvo_upgrade/drawings/Gehäuse 15.1 bottom alu plate.dxf
mesoSPIM_V5/inventor_files/60mm-blank-cageplate-LCP03M-Nikon-MOD.ipt
mesoSPIM_V5/inventor_files/Cube_30_with35hole.ipt
mesoSPIM_V5/inventor_files/CuvetteRack-250x144.ipt
mesoSPIM_V5/inventor_files/Galvomount-22mm-diameter-Left-Scanlab-V4.ipt
mesoSPIM_V5/inventor_files/Galvomount-22mm-diameter-Right-Scanlab-V4.ipt
mesoSPIM_V5/inventor_files/Galvomount-22mm-diameter-Thorlabs-Left.ipt
mesoSPIM_V5/inventor_files/Galvomount-22mm-diameter-Thorlabs-Right.ipt
mesoSPIM_V5/inventor_files/Large-cuvette-cap-25mm.ipt
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

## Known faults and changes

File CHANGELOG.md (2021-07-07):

(better late than never)
07.07.2021 A rack for cuvette storage has been added to [Wiki](https://github.com/mesoSPIM/mesoSPIM-hardware-documentation/wiki/Sample-storage).

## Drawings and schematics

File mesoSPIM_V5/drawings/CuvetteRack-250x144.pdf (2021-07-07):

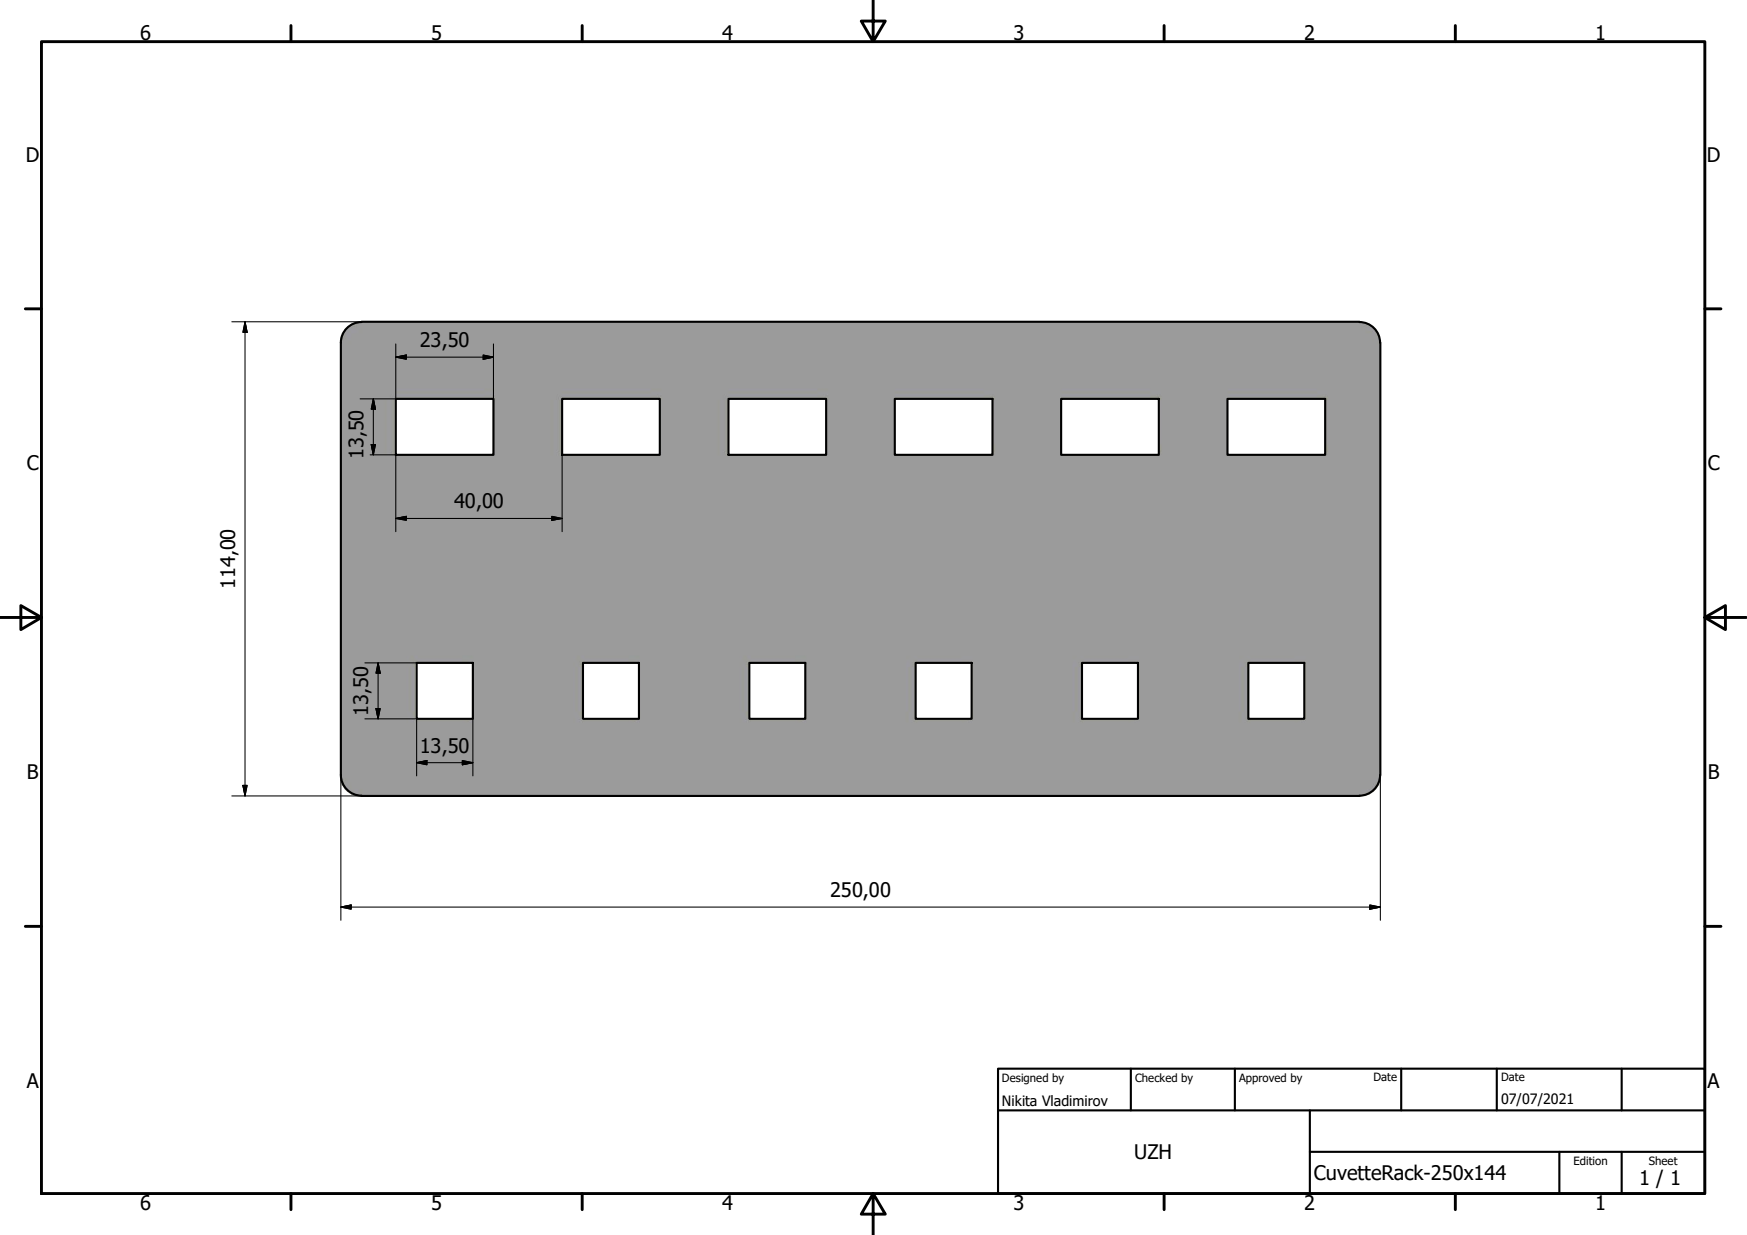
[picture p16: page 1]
CuvetteRack-250x144; UZH; Nikita Vladimirov; Designed by; Checked by; Approved by; Date; Edition; Sheet

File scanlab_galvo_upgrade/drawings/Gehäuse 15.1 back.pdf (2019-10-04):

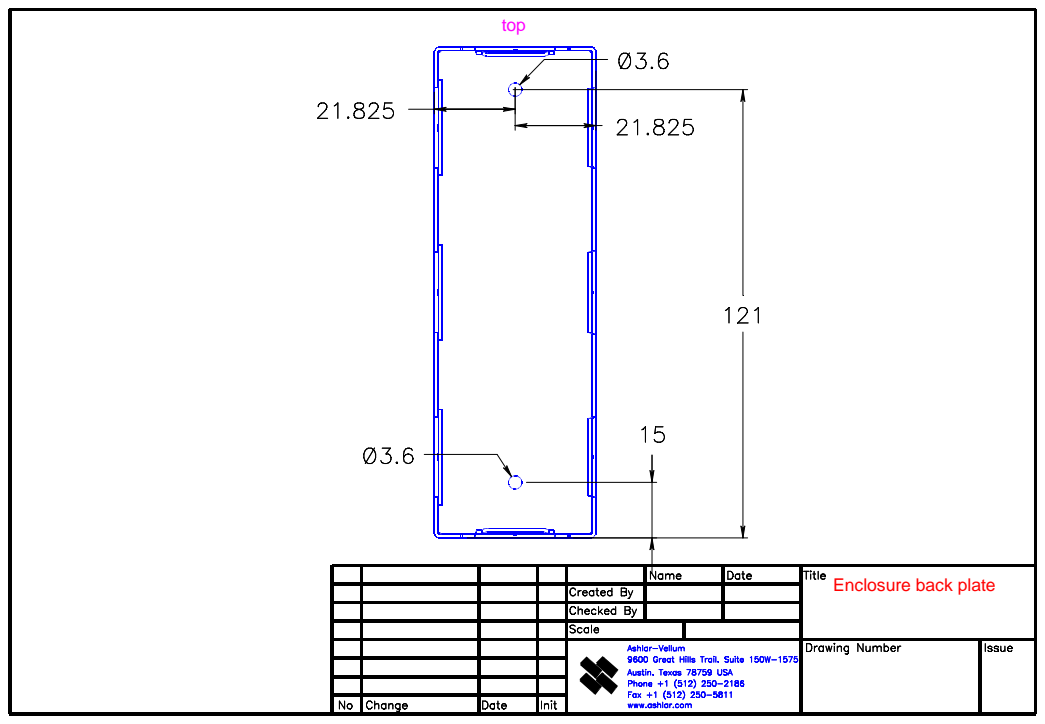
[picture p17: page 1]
top

Enclosure back plate

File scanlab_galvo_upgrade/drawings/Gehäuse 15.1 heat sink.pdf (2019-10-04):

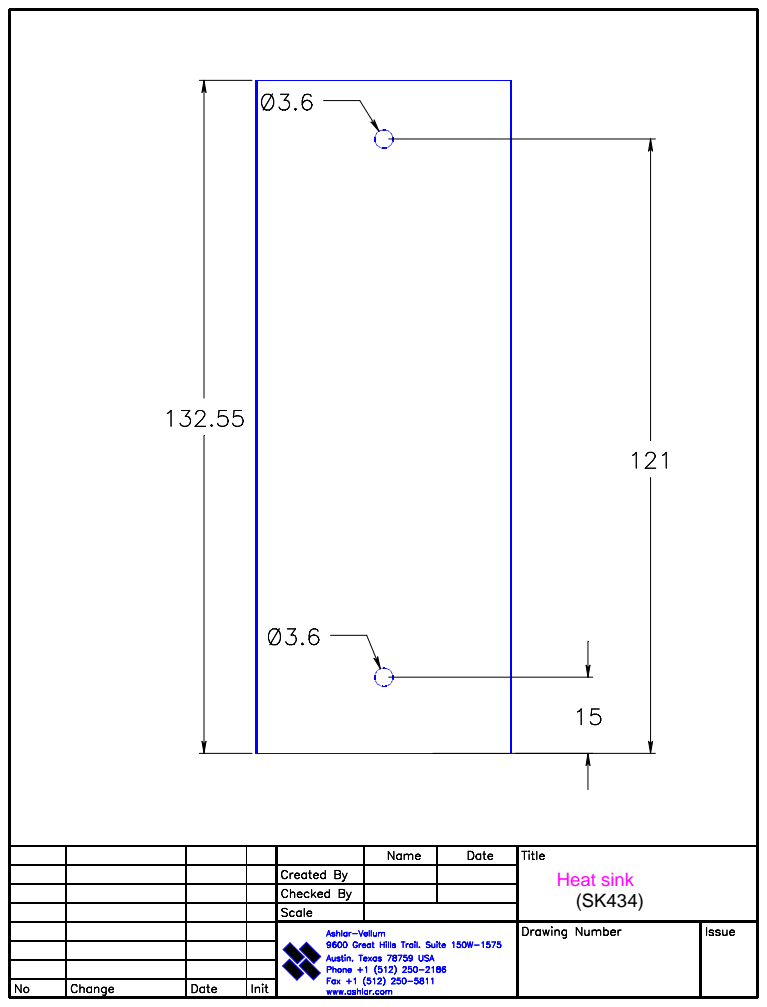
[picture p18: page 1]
Heat sink

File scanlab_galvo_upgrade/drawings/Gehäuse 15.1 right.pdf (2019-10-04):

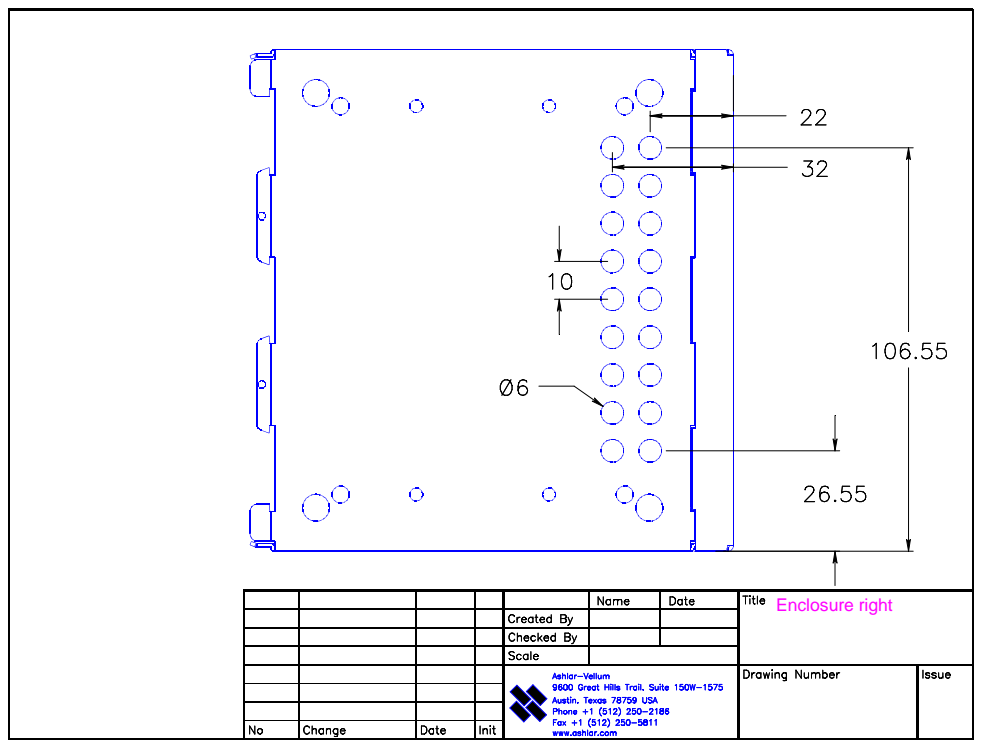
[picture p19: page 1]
Enclosure right

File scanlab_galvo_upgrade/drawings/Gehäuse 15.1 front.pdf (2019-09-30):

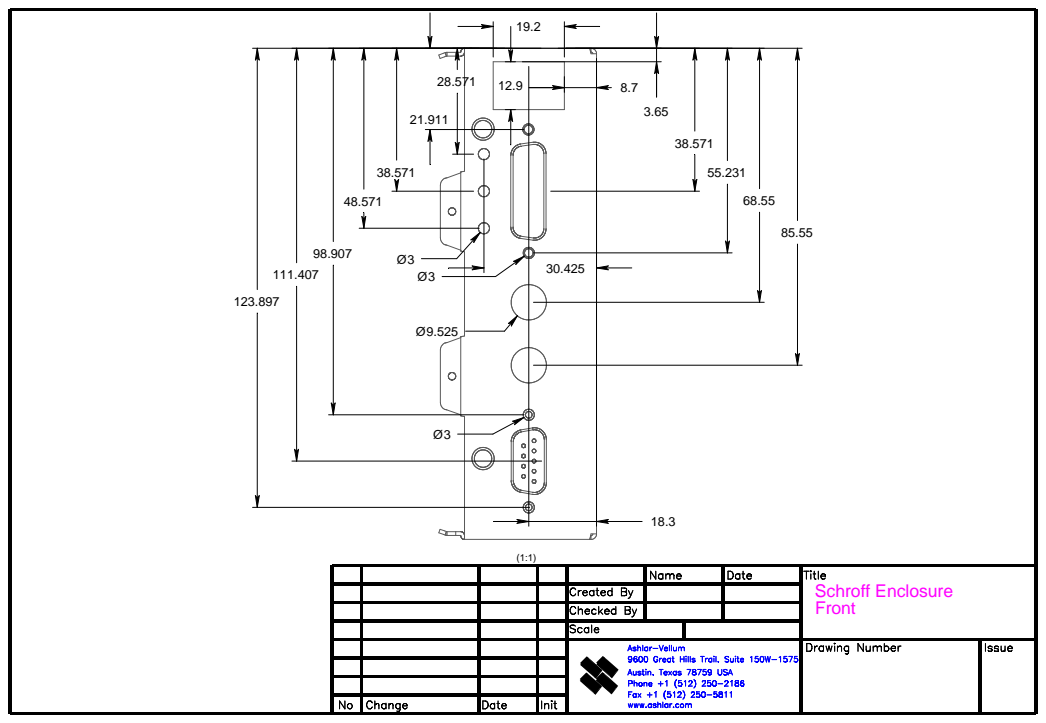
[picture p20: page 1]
Schroff Enclosure Front

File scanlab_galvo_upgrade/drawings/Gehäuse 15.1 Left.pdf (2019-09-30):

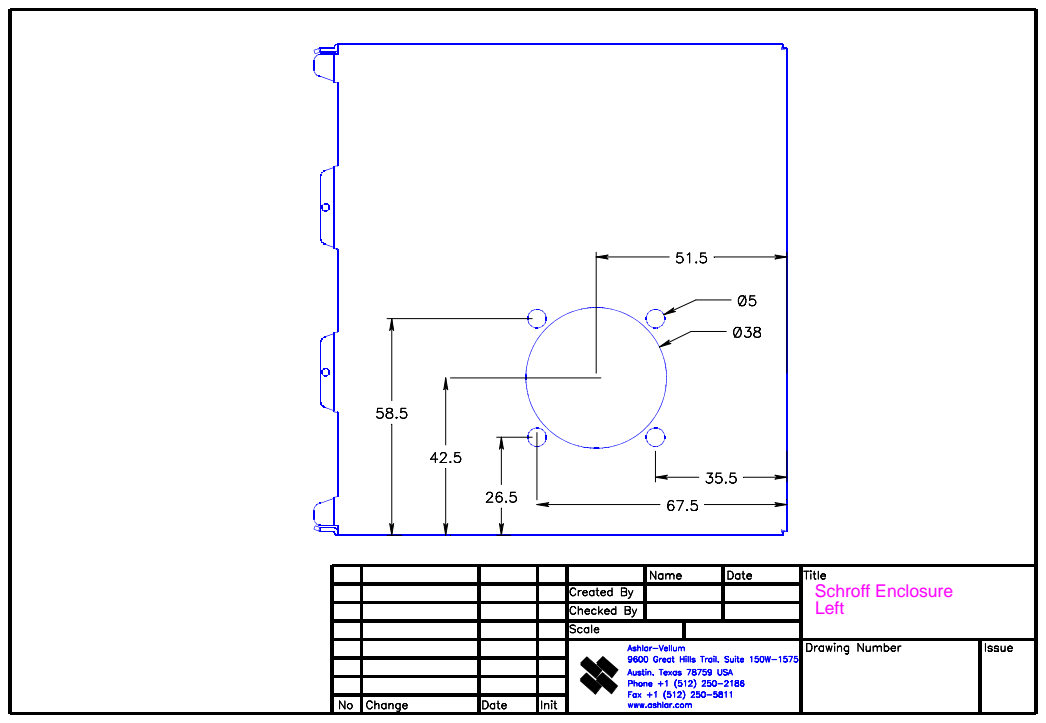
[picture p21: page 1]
Schroff Enclosure Left

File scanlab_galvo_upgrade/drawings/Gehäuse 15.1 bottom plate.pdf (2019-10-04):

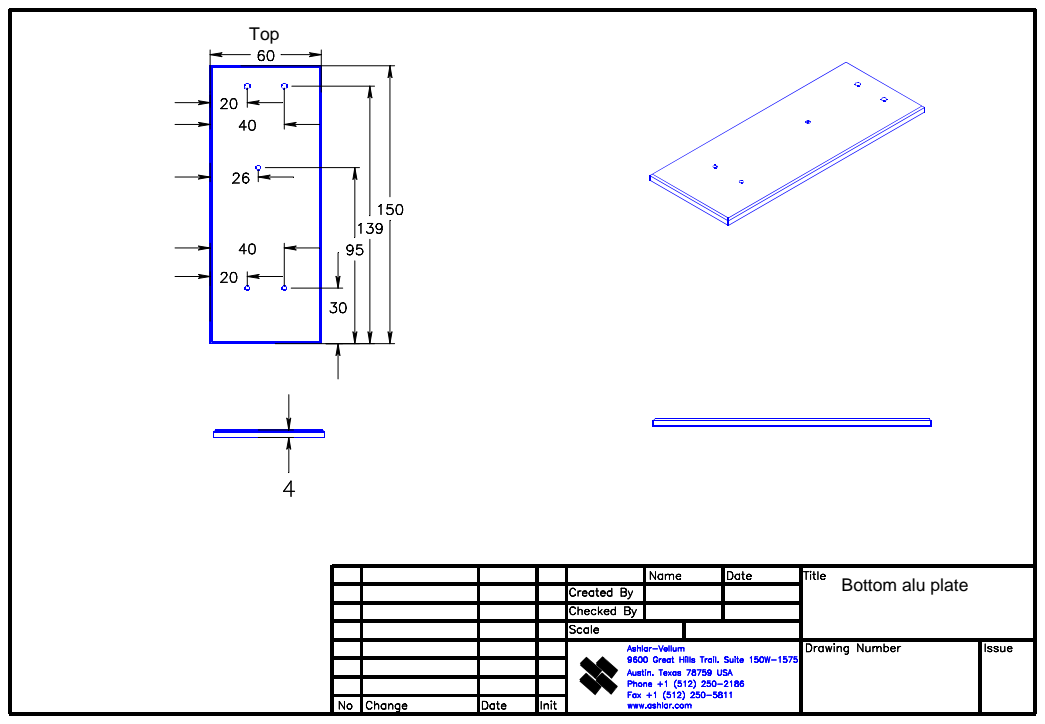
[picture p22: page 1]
Top

Bottom alu plate

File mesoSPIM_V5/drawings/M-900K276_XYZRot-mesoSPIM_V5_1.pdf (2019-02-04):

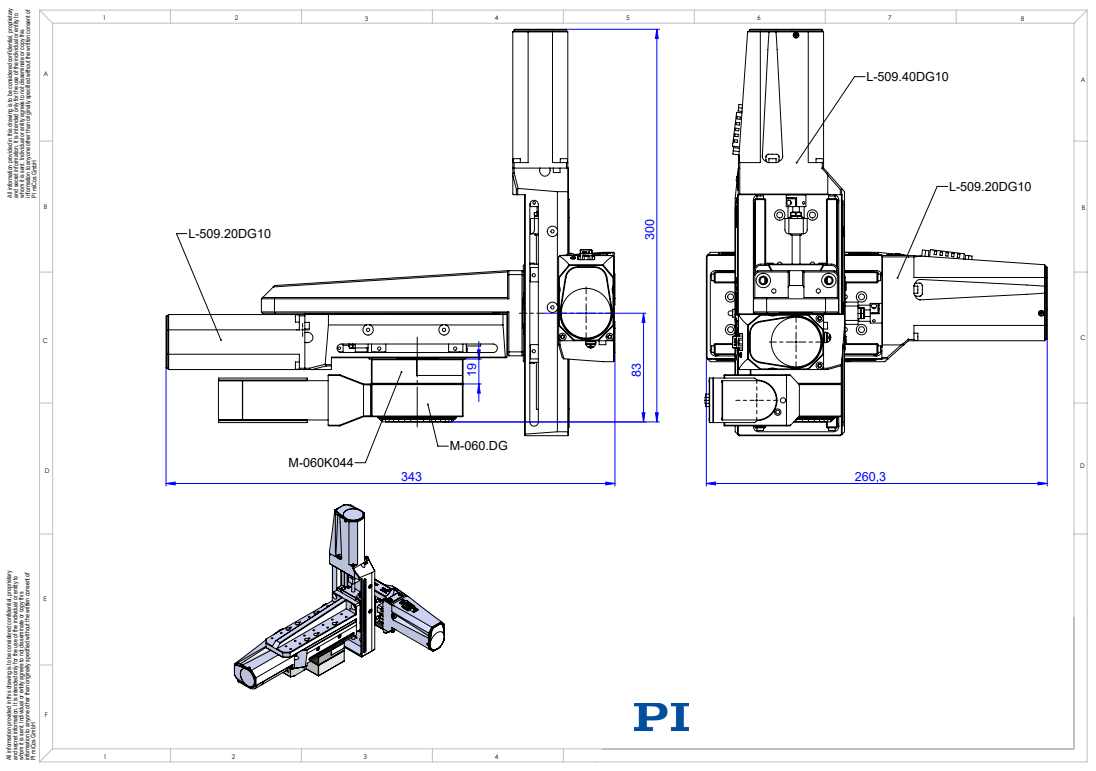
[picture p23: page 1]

All information provided in this drawing is to be considered confidential, proprietary and secret information. It is intended only for the use of the individual or entity to

whom it is sent. Individual or entity agrees to not disseminate or copy this information to anyone other than originally specified without the written consent of PI miCos GmbH

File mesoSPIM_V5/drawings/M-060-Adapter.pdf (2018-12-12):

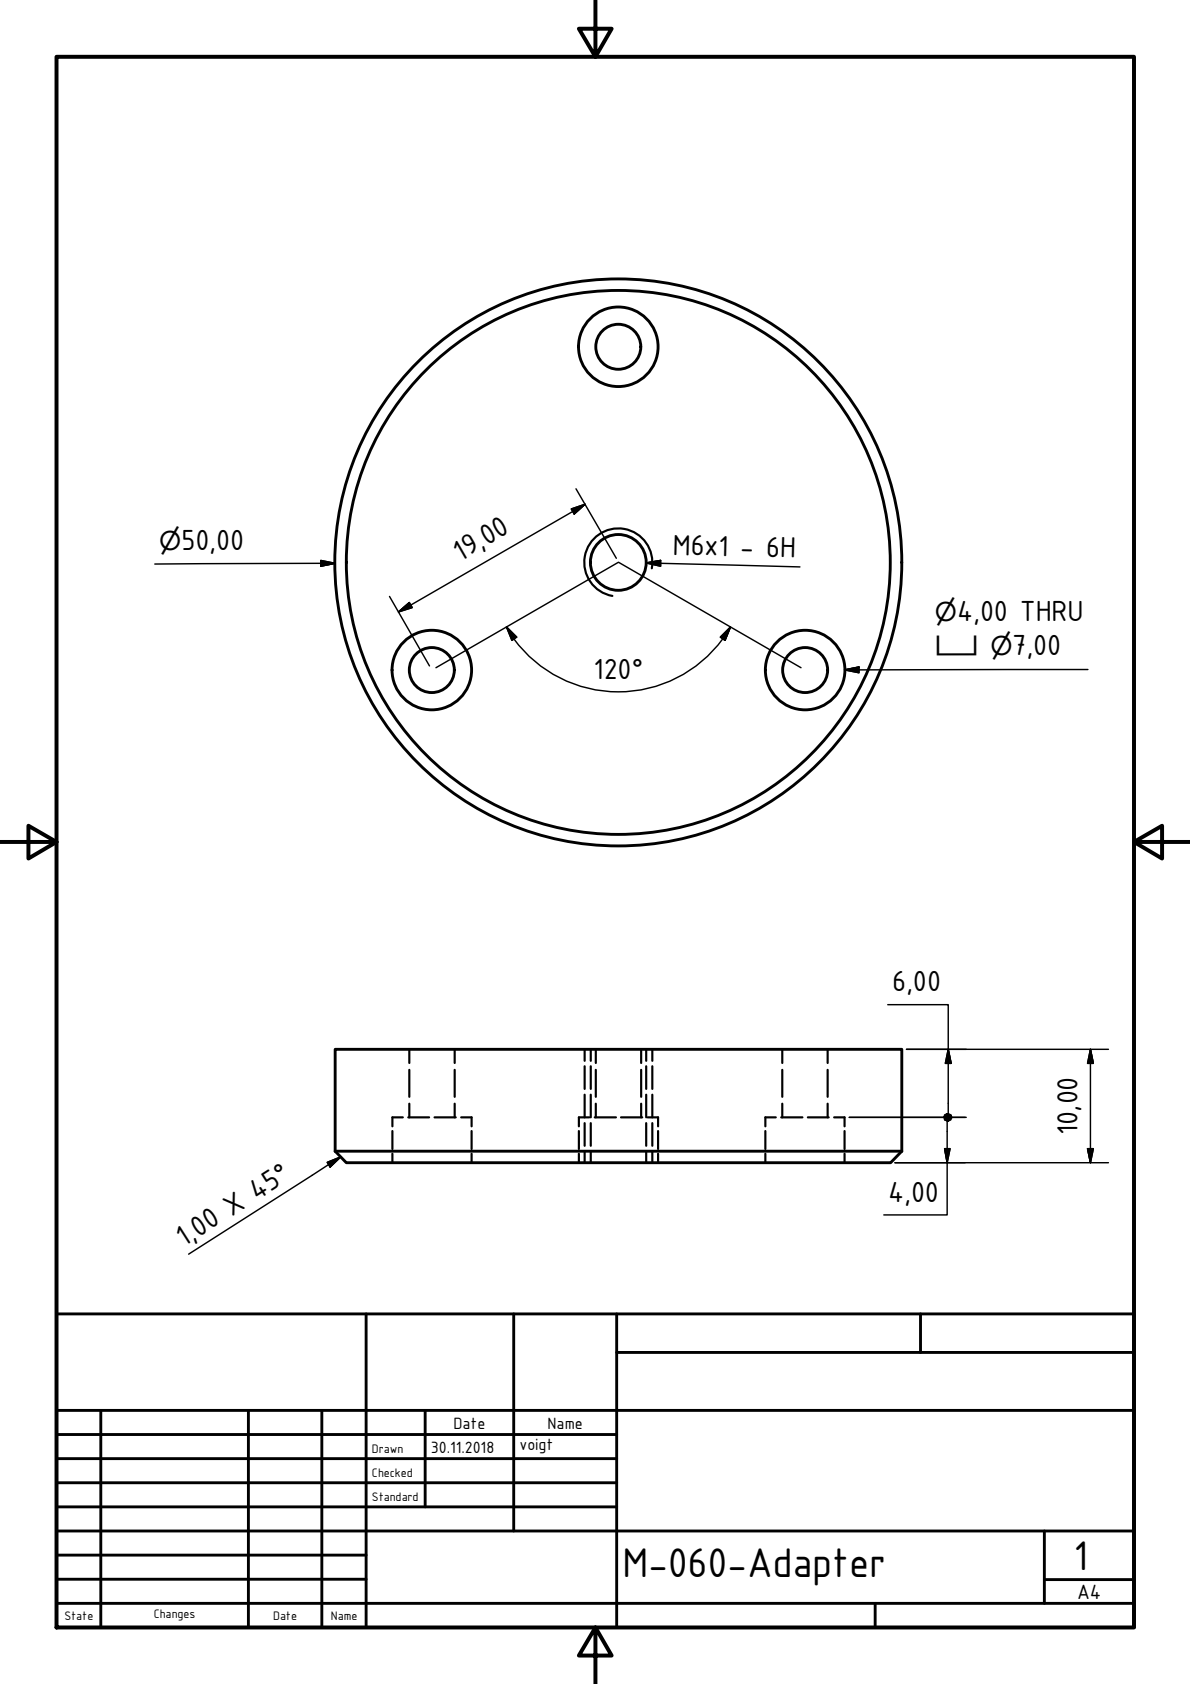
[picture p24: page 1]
M-060-Adapter; State; Changes; Date; Name; Drawn; Checked; Standard; voigt; P4,00 THRU X P7,00

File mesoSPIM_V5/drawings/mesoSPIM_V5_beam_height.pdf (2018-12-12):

1

2

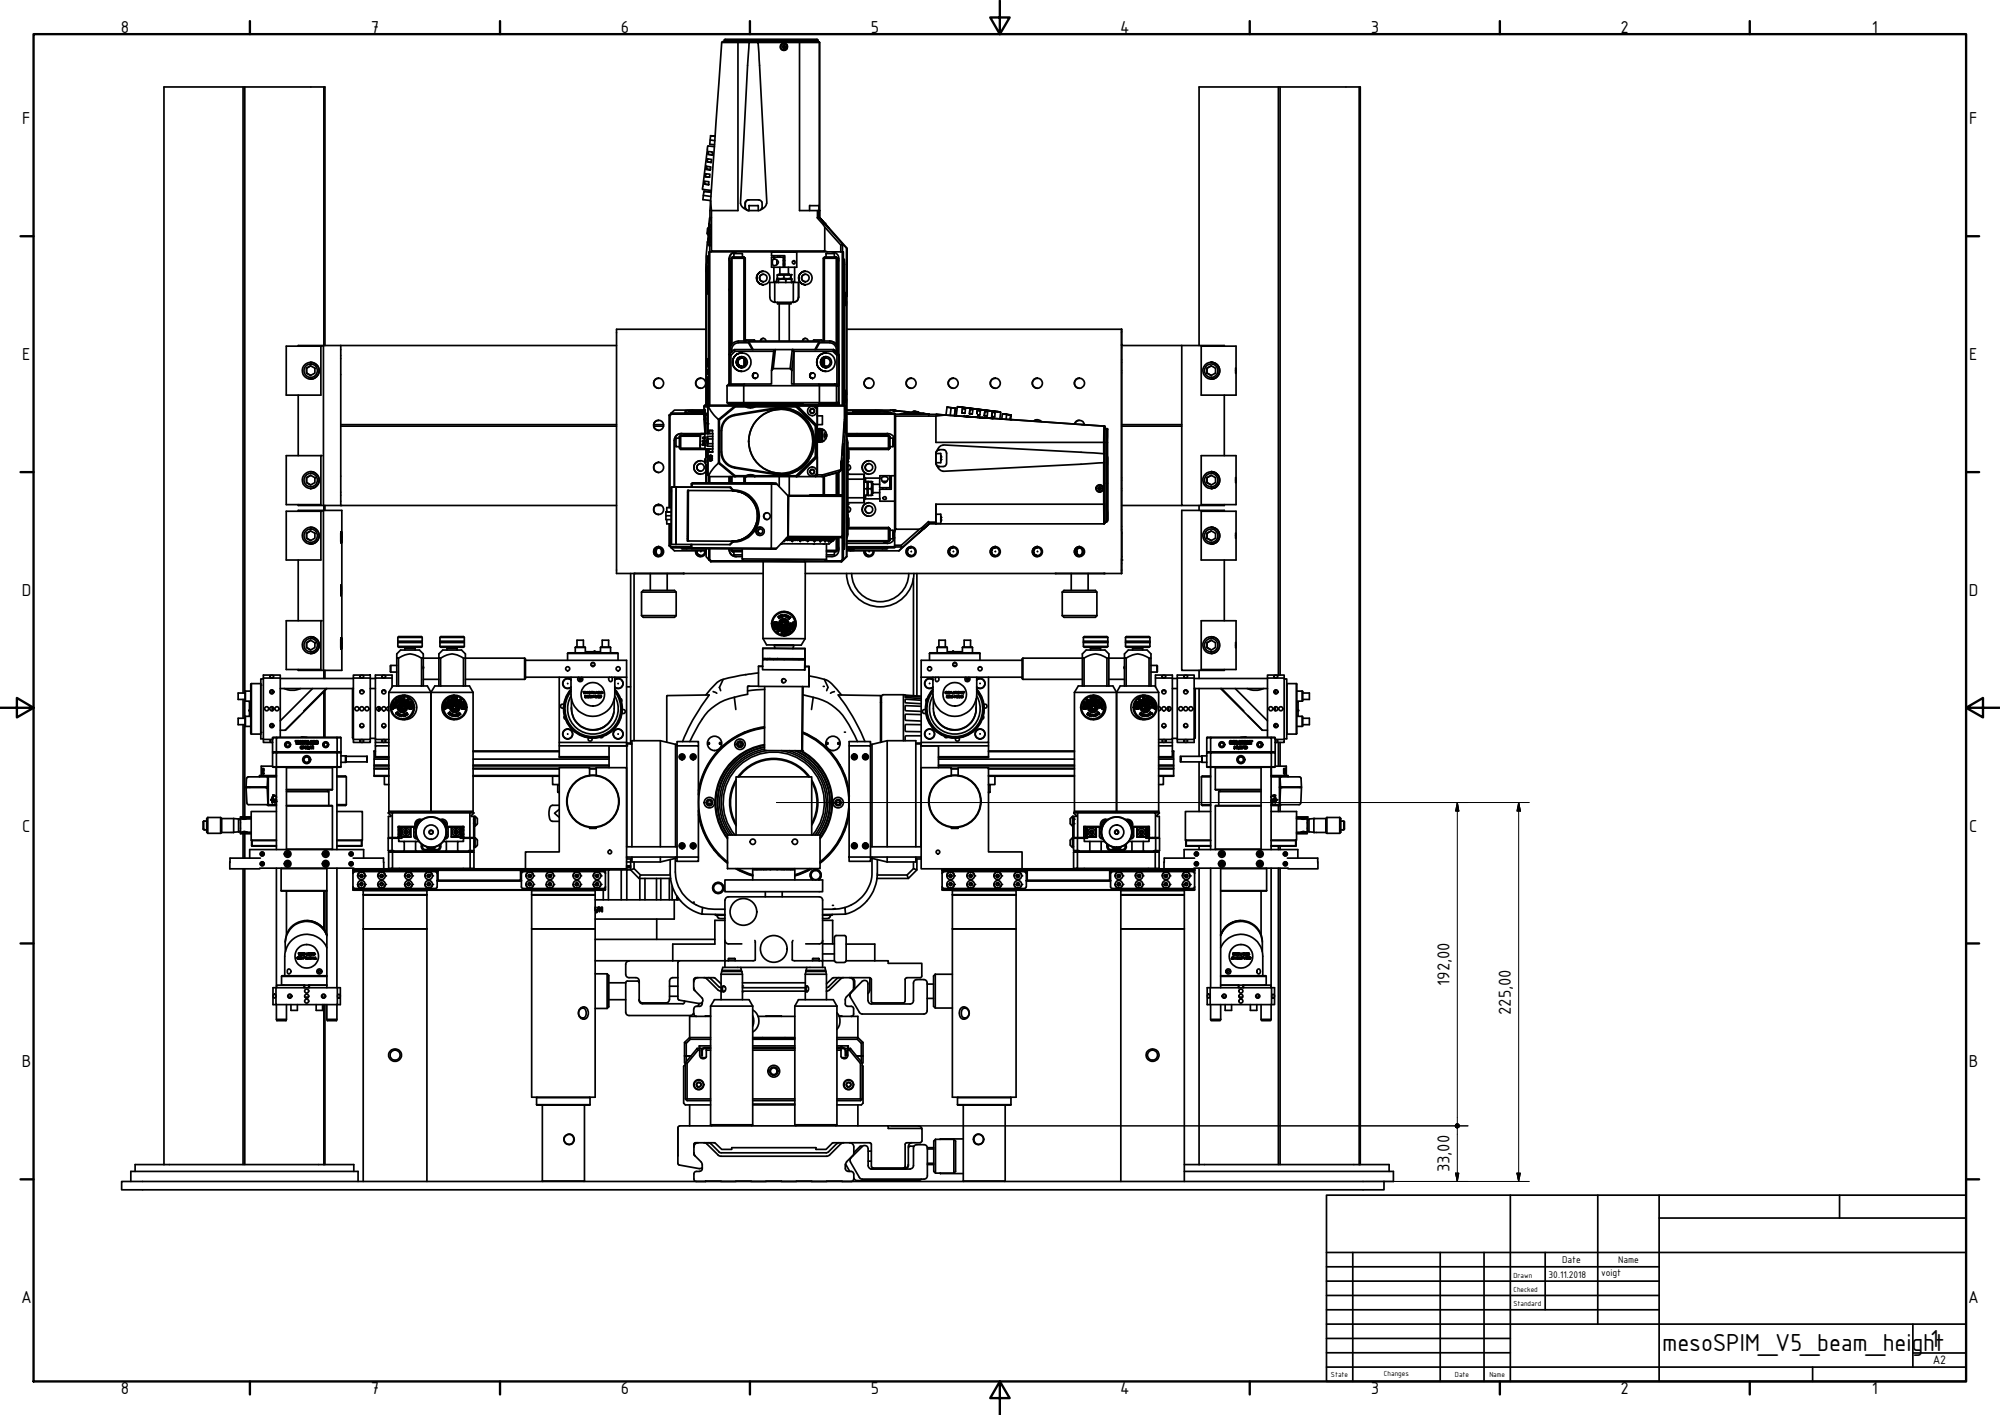
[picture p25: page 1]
mesoSPIM_V5_beam_height; State; Changes; Date; Name; Drawn; Checked; Standard; voigt

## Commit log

2018-12-12 Added parts lists
    [mesoSPIM-V4-parts-list-30-11-18.xlsx, mesoSPIM-V5-parts-list-12-12-18.xlsx]
2019-02-04 Added PI drawing of the mesoSPIM V5 stage set
2019-02-12 Added Inventor Files
    [60mm-blank-cageplate-LCP03M-Nikon-MOD.ipt, Cube_30_with35hole.ipt, Galvomount-22mm-diameter-Left-Scanlab-V4.ipt, Galvomount-22mm-diameter-Right-Scanlab-V4.ipt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]
2019-02-12 Added stp-files
    [60mm-blank-cageplate-LCP03M-Nikon-MOD.stp, Cube_30_with35hole.stp, Galvomount-22mm-diameter-Left-Scanlab-V4.stp, Galvomount-22mm-diameter-Right-Scanlab-V4.stp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]
2019-03-11 Added PI XYZ stage installation instructions
2019-05-08 Small updates to the parts list: Please use the most recent parts list
    [mesoSPIM-V5-parts-list-8-5-19.xlsx]
2019-09-30 drawings front and left
    [Gehäuse 15.1 front.dxf, Gehäuse 15.1 left.dxf]
2019-10-04 next file update
    [Gehäuse 15.1 back.dxf, Gehäuse 15.1 bottom alu plate.dxf, Gehäuse 15.1 right.dxf]
2019-10-07 pcb files for Dsub extension upload
    version 4 now and version 5 new and untested
    [scanlab_d-sub_extension_v4.brd, scanlab_d-sub_extension_v4.sch, scanlab_d-sub_extension_v5.brd, scanlab_d-sub_extension_v5.sch]
2019-11-07 Added 3D-printed iDISCO/BABB sample clamp
    [IDISCO-Sampleholder-12mm-60mm_V2.STEP]
2021-04-15 add STL files, README about dimensional accuracy
    [10x20mm_Cuvette_Top_V5_Sascha.stp, Large-cuvette-mount-30mm-V1.stl, Large-cuvette-mount-40mm-V3.stl, Large-cuvette-mount-40mm-V4_bottom.ipt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]
2021-04-15 tips of 3D printing materials
2021-04-26 added version 0.2 mm wider than the 40mm outer cuvette
    [Large-cuvette-mount-40mm-V4_top_extra0.2mm.ipt, Large-cuvette-mount-40mm-V4_top_extra0.2mm.stl]
2021-07-07 cuvette rack (sample storage)
    [CuvetteRack-250x144.ipt]
2022-02-22 clamp CAD files
    [Clamp-part1-Base9x19mm-maxSample28mm.ipt, Clamp-part1-Base9x19mm-maxSample28mm.stl, Clamp-part1-Base9x19mm-maxSample28mm.stp, Clamp-part1-Base9x19mm-maxSample4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]
2022-06-01 add compliant cuvette clamp (AddMan UZH design)
    [Clamp-UG205(204)_D100129(1mm Gelenke 2Stk.)_C.ipt, Clamp-UG205(204)_D100129(1mm Gelenke 2Stk.)_C.step, compliant-AddManDesign-D100129.SLDPRT]
2022-07-06 small sample clamp, base 9x10 mm; Cuvette-25mm mount.
    [Clamp-part1-base9x10mm-narrowTOP.ipt, Clamp-part1-base9x10mm-narrowTOP.stl, Clamp-part1-base9x10mm-narrowTOP.stp, Clamp-part2(moving)-Base9x10mm.ipt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]
2022-07-17 sample clamps: minor modifications for better friction (with smoothing and blackening)
    [Clamp-part1-Base9x19mm-maxSample40mm.ipt, Clamp-part1-Base9x19mm-maxSample40mm.stl, Clamp-part1-Base9x19mm-maxSample40mm.stp, Clamp-part1-base9x10mm-narrowTOP.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]
2022-09-05 sample clamps upload/update
    [Clamp-UG205(204)_100881(1mm Gelenke 2Stk.)_B.ipt, Clamp-UG205(204)_100881(1mm Gelenke 2Stk.)_B.step, Clamp-UG205(204)_100881(1mm Gelenke 2Stk.)_B.stl, Clamp-UG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]
2022-09-13 Miracca holder upload
    [clamp-base9x19mm-SampleH20mm-holdingScrewM4.ipt]
2022-09-13 Miracca clamp update
    [Clamp-base9x19mm-SampleH20mm-holdingScrewM4.stl, Clamp-base9x19mm-SampleH20mm-holdingScrewM4.stp, clamp-base9x19mm-SampleH20mm-holdingScrewM4.ipt]
2022-09-30 clamp update
    [Clamp-part2(moving)-Base9x10mm_flexible.step, Clamp-part2(moving)-Base9x19mm_flexible.step]
2022-12-08 upload newest sample holders
    [TopClamp-UG204_100943(Quadrat 2mm)_D.step, TopClamp-UG205_100943(Rechteck 2mm)_D.step]
2023-04-14 add large cuvette caps, for whole mouse storage/imaging
    [Large-cuvette-cap-25mm.ipt, Large-cuvette-cap-25mm.stl, Large-cuvette-cap-30mm.ipt, Large-cuvette-cap-30mm.stl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]
2023-09-15 create laser covers for V4-5 excitation arms (mirrors)
    [excitation-miror-cover-LEFT-Body.stl, excitation-miror-cover-LEFT.FCStd]
2023-09-18 extended by 30 mm sideways
    Update excitation-miror-cover-LEFT-Body.stl
    [excitation-miror-cover-LEFT-Body.stl, excitation-miror-cover-LEFT.FCStd]
2023-10-27 update parts list with new F-mount ring from Thorlabs SM2NFMA
    [mesoSPIM-V5-parts-list-latest.xlsx]
2023-12-14 large cuvette cap 3D print
    [Large-cuvette-cap-25mm.ipt, Large-cuvette-cap-25mm.stl]
2024-10-18 CBI Pittsburgh chamber
    [chamber-DLP-printed.STL]
